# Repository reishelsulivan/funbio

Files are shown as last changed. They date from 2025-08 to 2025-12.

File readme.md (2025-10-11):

# Fundamentos de Biodiseño  
## Grupo 8

<p align="center">
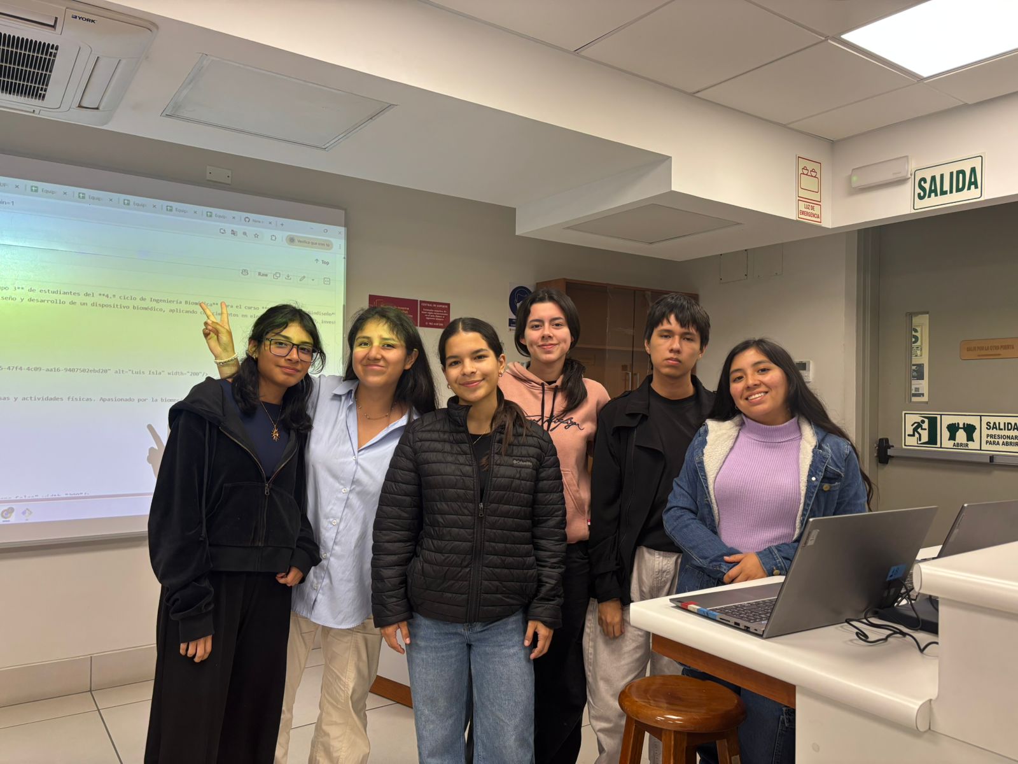
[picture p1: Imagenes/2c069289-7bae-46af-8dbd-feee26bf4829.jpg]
Imagen GRUPAL
  
</p>

*Grupo de estudiantes de Ingeniería Biomédica interesados en el desarrollo de nuevas tecnologías que favorezcan el avance médico.*

---

## 👥 Integrantes

### Reishel Sulivan Lope Paredes  
- **Edad:** 19 años  
<p align="center">
  Imagen REISHEL
</p>

---

### Murga Quispe, Jostin Rájhul  
- **Edad:** 18 años  
<p align="center">
  Imagen JOSTIN
</p>

---

### Daniela Alexandra Ochoa Cieza  
- **Edad:** 19 años  
<p align="center">
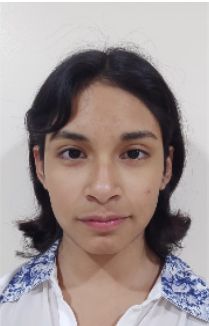
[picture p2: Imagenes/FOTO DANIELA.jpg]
Imagen DANIELA
  
</p>

---

### Sophia Nicole Nieves Maury  
- **Edad:** 21 años
- **Correo:** sophia.nieves@upch.pe 
<p align="center">
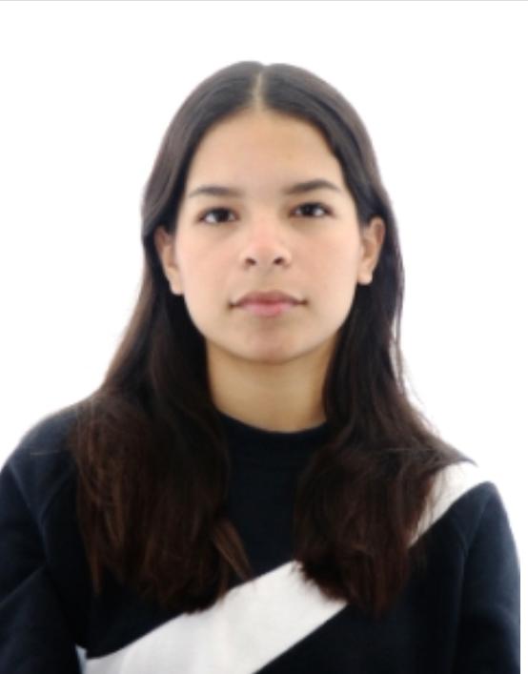
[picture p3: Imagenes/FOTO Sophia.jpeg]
Imagen NICOLE
  
</p>

---

### Sharon Lizeth Oré Arredondo  
- **Edad:** 18 años  
<p align="center">
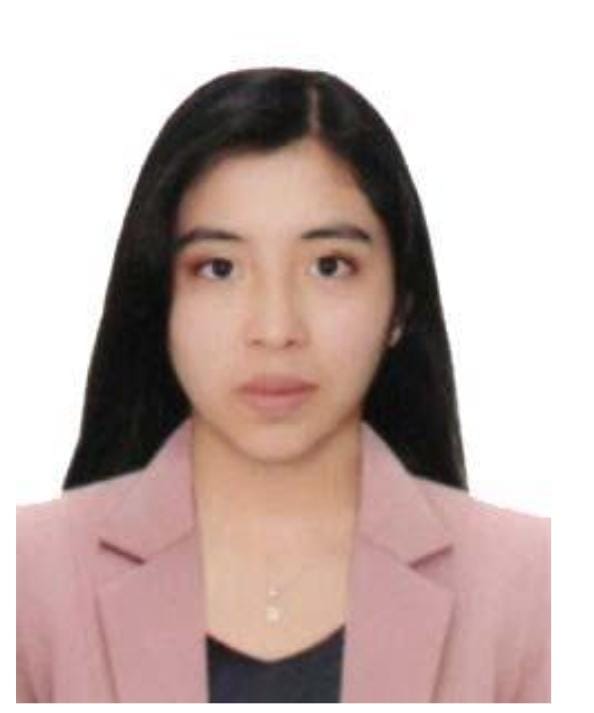
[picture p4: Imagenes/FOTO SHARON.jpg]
Imagen LIZETH
  
</p>

---

### Maria del Carmen Paredes Cavero  
- **Edad:** 20 años  
<p align="center">
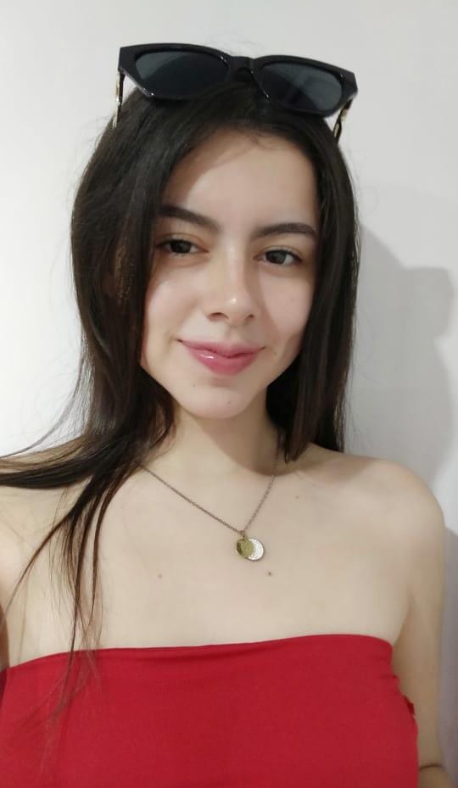
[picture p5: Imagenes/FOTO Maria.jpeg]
Imagen MARIA
  
</p>

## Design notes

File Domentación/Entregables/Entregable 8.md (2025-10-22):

<div align="center">

# Fundamentos de Biodiseño: Entregable Nº 8

</div>
<div align="center">
  
## Sección 2: Modelado 3D
</div>

### Sensor ESP32:
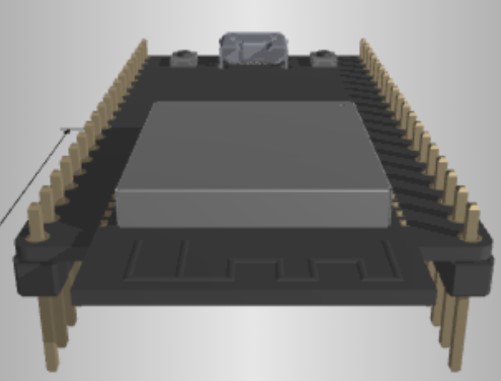
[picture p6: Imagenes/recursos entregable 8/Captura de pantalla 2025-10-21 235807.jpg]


https://cad.onshape.com/documents/9392f3b08a5a12f459dcdf1e/w/5ffc1e2daefd1c3cd6f5d1c5/e/543962da6f37cdc580fbc518?renderMode=0&uiState=68f86065a9befacfd8228599

### Sensor de Temperatura TMP36
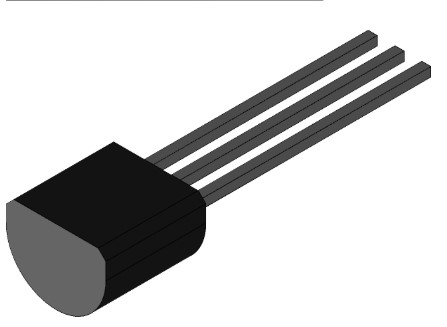
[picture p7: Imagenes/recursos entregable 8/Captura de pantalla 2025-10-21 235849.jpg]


https://cad.onshape.com/documents/74f086d47442c8f6e3b532a9/w/f83696dc04ceff2c60df9320/e/4f5c1f82b5e9618f5d499a5d?renderMode=0&uiState=68f86093083b60e7112f9d35
### FSR 400
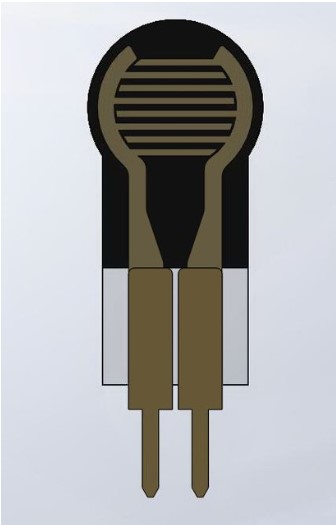
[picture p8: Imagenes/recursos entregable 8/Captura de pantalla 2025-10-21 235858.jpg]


https://cad.onshape.com/documents/1bdf3e697803877b7e2c2b3c/w/df2d8b826d9c72e3113c0d29/e/82d6d8926c4703dbe4e6c42b?renderMode=0&uiState=68f860b1e923a8006b744c4f
### TP4056 module
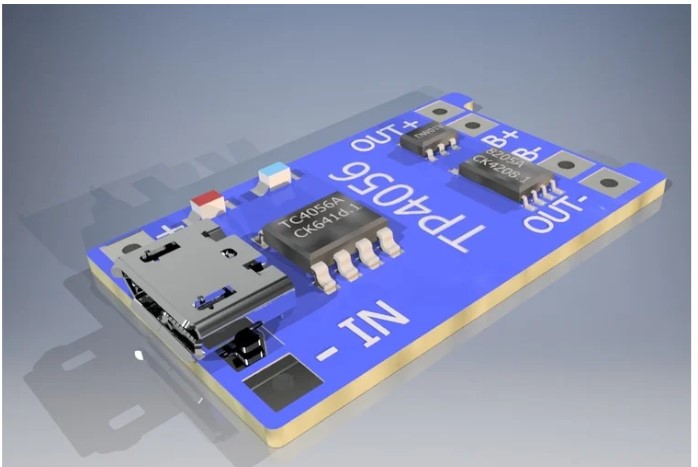
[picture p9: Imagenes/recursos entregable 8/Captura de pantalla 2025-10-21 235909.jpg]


https://cad.onshape.com/documents/18cd05a88509de23cd2a2f93/w/8d196be95ea5bc2b3ad85955/e/2d019528366bb7ebba015902?renderMode=0&uiState=68f863c543911c5820f0d8de
### MT3680 module
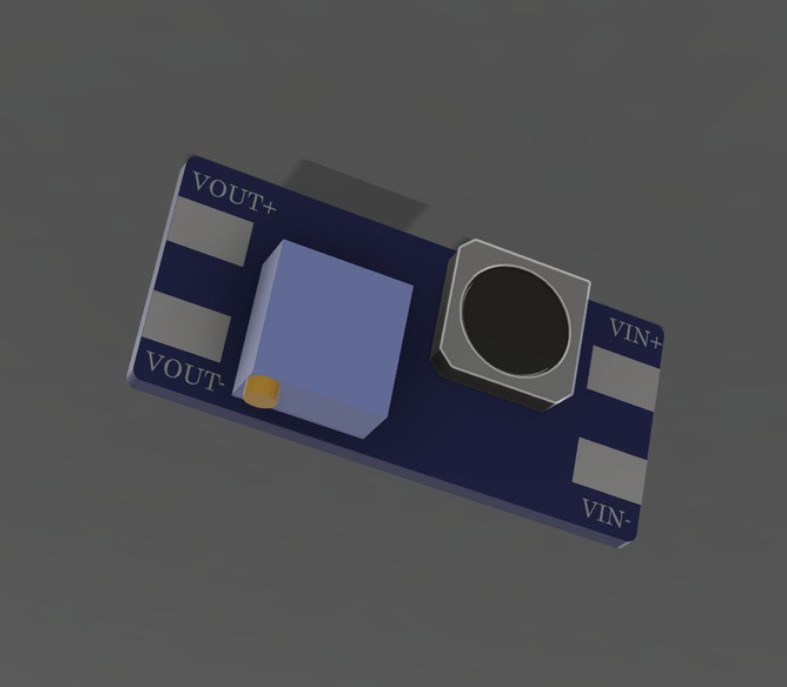
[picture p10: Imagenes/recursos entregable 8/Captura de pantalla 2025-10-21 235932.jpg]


https://cad.onshape.com/documents/760e85918c161715fd75b83e/w/cb98ee53cf6b21a846fe382e/e/080db2f108718dd84d546821?renderMode=0&uiState=68f865730297eada4858e549
### Case Principal
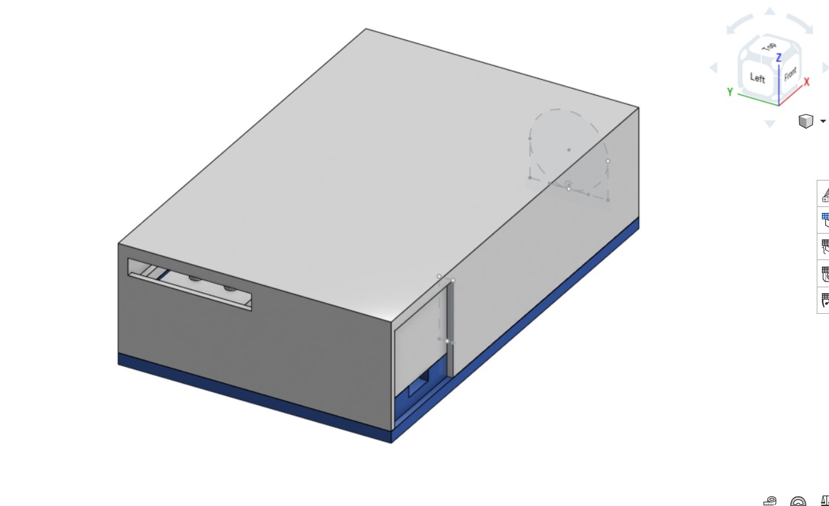
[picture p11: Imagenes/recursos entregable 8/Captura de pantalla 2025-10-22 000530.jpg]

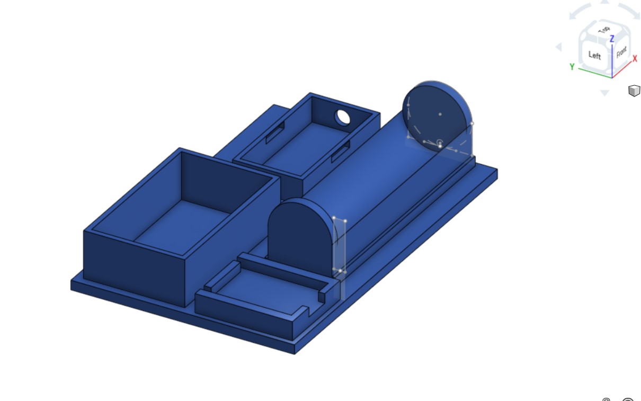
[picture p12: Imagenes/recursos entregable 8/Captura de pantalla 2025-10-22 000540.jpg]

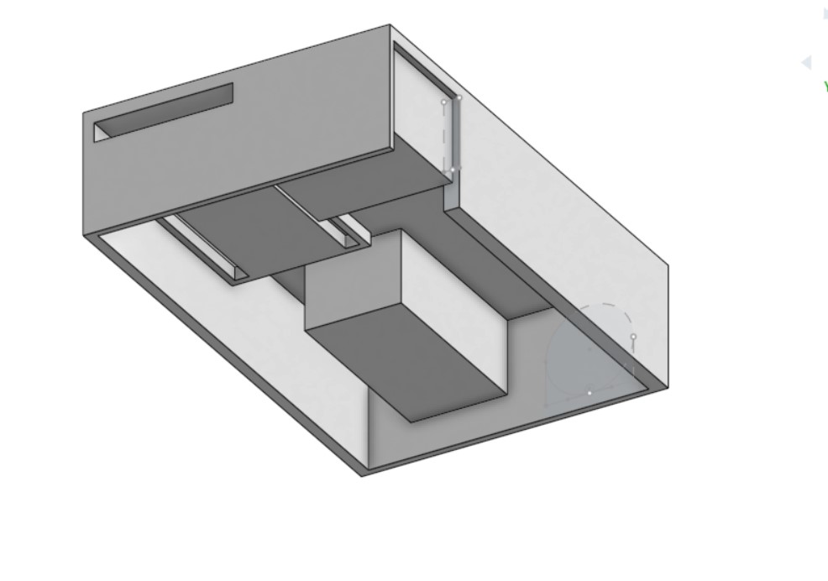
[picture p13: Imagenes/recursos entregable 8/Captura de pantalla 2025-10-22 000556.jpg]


https://cad.onshape.com/documents/a6e36f7cac065b05814f1a20/w/e1e7ecee820c783deadf52ee/e/a61f189e7a23719cba901df4?renderMode=0&uiState=68f8658543911c5820f0db09
### Case FSR
Texto alternativo

### Case Motor de vibracion
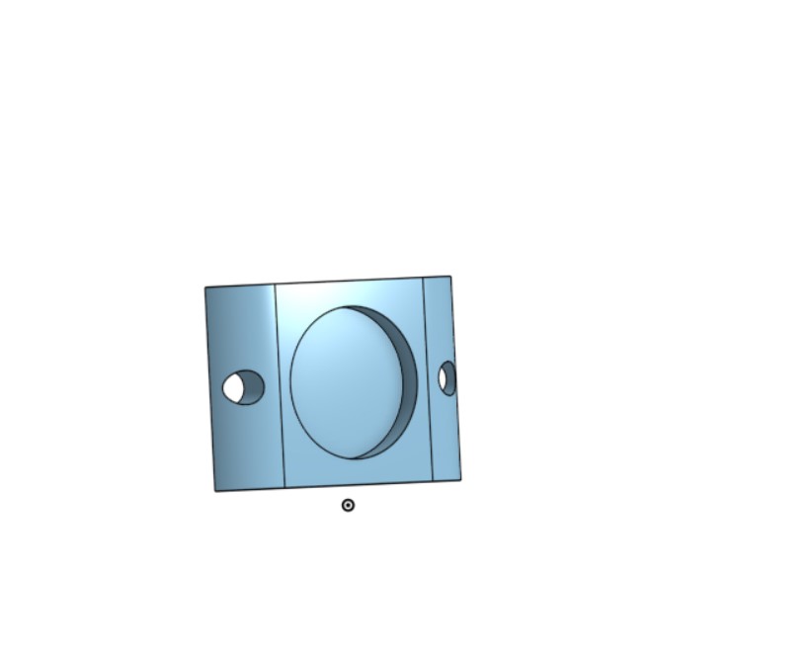
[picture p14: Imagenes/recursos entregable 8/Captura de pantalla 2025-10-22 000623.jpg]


https://cad.onshape.com/documents/7fd997337caf7b52a8c2670a/w/bb5fb6264d26da24b70b61d7/e/f94ade3b7513662598104bfb

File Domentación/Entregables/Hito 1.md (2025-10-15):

<div align="center">

# Fundamentos de Biodiseño: Hito N°1

</div>

<div align="justify">

## 1. Modelos y principios de solución
| **Función**              | **Solución 1**              | **Solución 2**              | **Solución 3**             |
|---------------------------|-----------------------------|-----------------------------|-----------------------------|
| **Distribuir presión**    | Espuma viscoelástica        | Gel de silicona             | Air cushion                 |
| **Reducir fricción**      | Tejido de poliamida         | Tejido de poliéster         | Tejido de algodón           |
| **Absorber sudor**        | Material absorbente         | Canales de ventilación      | Malla 3D transpirable       |
| **Monitorizar presión**   | FSR                         | FlexiForce                  | Sensor capacitivo           |
| **Monitorizar temperatura** | Termistor                 | Sensor infrarrojo           | RTD                         |
| **Fácil poner/quitar**    | Cierre magnético            | Cierre de velcro            | Cremallera                  |
| **Lavable**               | Material impermeable        | Funda desmontable           | Material resistente          |

## 2. Espacio de solución

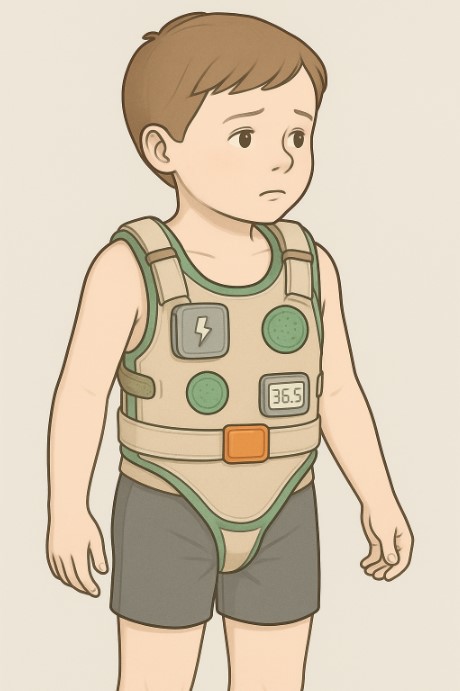
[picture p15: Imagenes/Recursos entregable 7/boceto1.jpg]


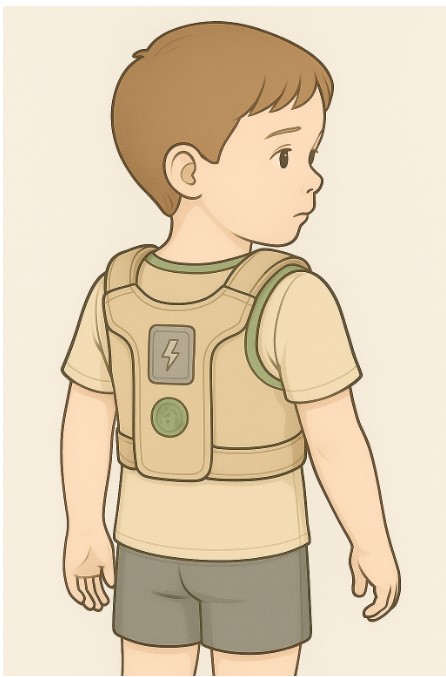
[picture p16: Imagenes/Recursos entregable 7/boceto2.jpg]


## 3. ¿Fabricar o adquirir?:
- Sensor de presión — Adquirir. Se comprará un sensor de presión presente en el mercado, preferiblemente el FSR
- Microcontrolador — Adquirir. Se comprará un microcontrolador ESP32
- Batería - Adquirir
- Carcasa para electrónica - Fabricar. Se fabricará únicamente una carcasa para el microcontrolador y sensores.
- Material para el liner - Adquirir.  Se adquirirá el material del liner.
- Fabricación del liner — Fabricar. Se fabricará el liner con costura.

## 4. Secuencia de procesos:
Describir la rutina clínica de uso del sistema
- Montaje en el paciente
	- El fisioterapeuta prepara la piel del bebé 
	- Se posiciona el liner con sensores dentro del corsé, asegurando que las zonas de presión coincidan con los puntos anatómicos indicados por el médico.
	- Se conecta el módulo electrónico (SPS) a los conectores del liner.
	- Se verifica que todo esté bien colocado y conectado con el recurso de monitoreo
- Calibración
	- Antes de iniciar, se enciende el módulo electrónico y se conecta al recurso de monitoreo.Se realiza una calibración inicial de presión y temperatura, asegurando que las lecturas correspondan al estado de reposo del paciente.
	- Durante esta fase (≈10–15 segundos), el niño permanece quieto para registrar el nivel base de presión y temperatura.
	- A continuación, el fisioterapeuta comprueba la reacción de los sensores ejerciendo suaves presiones manuales en los puntos clave del corsé; el sistema debe mostrar los cambios instantáneamente.
	- Si se detectan lecturas fuera del rango previsto, se ajusta el liner o el corsé hasta alcanzar uniformidad en las áreas sensorizadas.
Se guarda la calibración y se comienza la terapia.
- Sesión de terapia
	- Durante su uso, el sistema mide con el sensor de presión cada 2 segundos y el de temperatura cada 10 segundos, recolectando información suficiente para analizar la distribución de carga y el confort térmico del paciente.
	- Los datos se envían de forma inalámbrica al recurso de monitoreo clínico, donde el fisioterapeuta puede observar las lecturas en tiempo real o analizarlas posteriormente.
	- Si se detecta un aumento de presión o temperatura (por mala colocación o exceso de sudor), el sistema envía una alerta visual en el recurso de monitoreo, indicando la necesidad de reajustar el corsé.
- Desmontaje
	- Se apaga el sistema, se desconecta del liner y se retira cuidadosamente el corsé del bebé.
	- Se retira el liner del corsé si se requiere limpieza o cambio.
- Limpieza:
	- Antes del lavado, se retiran el módulo electrónico (SPS), los sensores removibles, los cuales se limpian por separado con un paño suave humedecido en alcohol isopropílico al 70 % o con toallitas médicas, sin sumergirlos en agua.
	- Una vez limpio y seco, se vuelve a insertar la electrónica en sus respectivos bolsillos sellados y se verifica su funcionamiento mediante el recurso de monitoreo antes del siguiente uso.
**Diagrama de flujo**
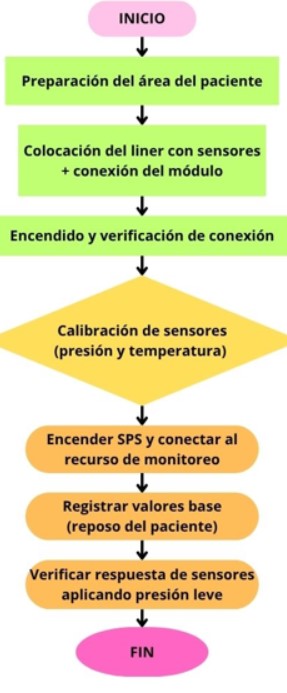
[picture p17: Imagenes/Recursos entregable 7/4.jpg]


## 5. Técnicas de producción

**Electrónica:**
- ESP32.- Se utilizará impresión 3D de polímeros biocompatibles como una carcasa para evitar la incomodidad en el bebé .
  - Costos:  	Debido a que se trabaja con impresión 3D  no requiere de moldes por lo que solo 
		emplea el material necesario sin adicionar costos. Los costos de su producción   
		pueden estimarse entre 2 y 5 dólares por unidad dependiendo del material .
  - Durabilidad: Se optimiza su durabilidad y correcto funcionamiento ya que no se  encuentra expuesto ante caídas o derrame de líquidos .
Facilidad de esterilización: Algunos de los polímeros biocompatibles resisten los procesos de esterilización sin que se dañen o degraden ya que materiales como PETG y PEEK soportan temperaturas de hasta 120 °C. Sumado a esto, se reduce la acumulación de microorganismos debido a su superficie lisa .

## 6. Estaciones de trabajo
Gimnasio  de terapia : Esta estación de trabajo consiste en realizar ejercicios personalizados  de rehabilitación y terapéuticos. Tiene como objetivo recuperar o mejorar la funcionalidad , fuerza o movilidad del paciente .
Es importante que la adquisición del liner vaya acompañada de estas terapias para asegurar una correcta movilidad del paciente de forma cómoda y segura sin riesgo de irritar la piel .
Por otro lado ,para estas sesiones, el especialista debe tener a disposición un dispositivo que le permita monitorear y verificar el correcto funcionamiento del accesorio (ej. bluetooth activado) antes de iniciar con la sesión para evitar incomodidad al momento de realizar los ejercicios. Además , evitar usar en simultáneo equipos de electroterapia o magnetoterapia . 

## 7.Automatización
El sistema cuenta con un nivel medio de automatización, ya que proporciona retroalimentación a través de sensores de temperatura, presión y humedad integrados en el acolchado removible, brindando información útil tanto al grupo médico especializado que supervisa los registros como a los padres o cuidadores, mediante una aplicación comprensible. 
Técnicamente, un nivel medio garantiza que el dispositivo se encargue de interpretar  los datos sensoriales y brinde avisos si se detectan cambios en las condiciones internas (como humedad o temperatura elevada) o presión inadecuada. Esto reduce riesgos y mejora la eficacia del tratamiento, sin reemplazar el criterio profesional. 
Desde el punto de vista clínico, esta elección es adecuada porque el paciente es un niño, y se requiere un equilibrio entre asistencia tecnológica y control humano. El sistema busca facilitar el trabajo terapéutico y permitir al personal especializado evaluar la evolución de la escoliosis congénita del paciente, manteniendo la seguridad y comodidad. Además, la aplicación permite generar reportes diarios, cada tres días o semanales, según lo decida el usuario, facilitando el seguimiento del tratamiento y el monitoreo de la evolución del paciente.
Con respecto a los escenarios de seguridad, en caso de que se detecte una condición anormal —como aumento de temperatura o humedad excesiva— la alerta se enviará automáticamente a través de la aplicación. Esto indica que el sistema está cumpliendo su función de detección. Solo si se presentan falsos positivos, se debe reportar al recurso de monitoreo para que se realice una revisión técnica y se garantice el correcto funcionamiento del dispositivo. Los padres o cuidadores no deben manipular la parte electrónica, ya que requiere conocimientos técnicos.
En caso de falla del sistema, los sensores dejarán de emitir datos y el módulo entrará en “modo inactivo”, evitando lecturas erróneas y posibles confusiones. Por ello, no se requiere un botón de parada de emergencia, debido a que el dispositivo no cuenta con componentes motorizados que representen un riesgo activo. La seguridad se respalda mediante la supervisión del personal especializado y el diseño ergonómico y acolchado del corsé, que evita puntos de presión excesiva y mantiene la comodidad del paciente.

## 8.Interfaces de red global(IoT y telesalud)
### 1.  Sistema y recolección de datos
#### Sensores
i. Sensor de presión (en el punto crítico del corsé): mide la fuerza normal (en Newtons). Su señal analógica entra al convertidor ADC del ESP32 a una tasa típica de 10–50 Hz, lo cual es suficiente para detectar cambios graduales y picos por apriete.
ii. Temperatura del módulo (MCU): un termistor/sensor ubicado cerca de la electrónica/batería para seguridad térmica. Lectura periódica ( cada 1–2 s por ejempl).

#### Microcontrolador ESP32
i. Adquisición: digitaliza presión (ADC) y lee temperaturas (1-Wire/I²C).
ii. Procesamiento: calcula promedios, máximos y banderas (en uso / presión excesiva / temperatura alta).
iii. Reglas con temporización (de esta manera se evitan falsos positivos):
- Uso: presión promedio por encima del umbral de uso durante 2–3 s.
- Presión excesiva: presión por encima del umbral de presión ≥ 3 s.
- Temperatura MCU alta: Tmcu > Tmcu_max ≥ 5 s.
	
iv. Comunicación:
- Bluetooth (activo de manera continua): envía notificaciones inmediatas al celular de los padres. Si el enlace se corta, el ESP32 reintenta y acumula alertas para el siguiente envío.
- Wi-Fi (cuando esté disponible): envía reportes en formato CSV y un resumen de manera diaria a una hora programada o cuando aparece una anomalía.

#### Celular de los padres (Bluetooth)
i. Mantiene una conexión BLE (Bluetooth Low Energy) en segundo plano.
ii. Recibe notificaciones push
- Presión excesiva en el punto
- Temperatura corporal alta
- Módulo caliente, revisar equipo
iii. Muestra el estado (“En uso” / “No en uso”)

#### Servidor/PC del terapeuta (Wi-Fi)
i. Recibe reportes automáticos (diarios o por anomalías) en formato tipo CSV crudo y una hoja de resumen lista para graficar.
ii. Posible inclusión de vistas con curvas de presión/temperaturas y marcadores de eventos.

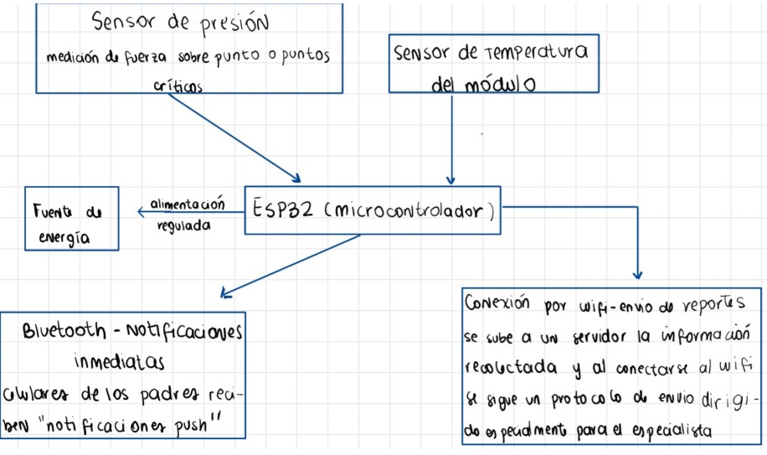
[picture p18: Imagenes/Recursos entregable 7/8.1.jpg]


### 2.  Información recolectada
El sistema registra dos señales y metadatos operativos. En primer lugar, la presión en el punto crítico del corsé (en N), con muestras entre 10 y 50 Hz y suavizada con promedio móvil para atenuar el ruido; a partir de ella se determina el estado de uso cuando el promedio supera un umbral de uso durante algunos segundos, y se detecta presión excesiva cuando la señal permanece por encima del umbral clínico de presión con un tiempo mínimo para evitar falsos positivos. En segundo lugar, la temperatura del módulo electrónico (en °C), medida cerca de la electrónica o la batería a intervalos de 1–2 s, que permite identificar sobrecalentamiento del dispositivo si rebasa el umbral de temperatura por un lapso definido. Además se almacenan metadatos por registro (sello de tiempo, código anónimo del paciente, estado de conectividad Bluetooth/Wi-Fi y eventos como inicio, pausa, fin o alertas) en formato CSV/Excel para análisis y generación de reportes diarios o al detectar anomalías.	

### 3. Reportes para el terapeuta
Esta tabla es el encabezado del reporte que recibirá el especialista. Cada fila resume una lectura con identificadores anónimos y variables clave: Sesión (código de la sesión), Paciente (código anónimo), Fecha en formato ISO (sin ambigüedades horarias), presión_N (fuerza en Newtons sobre el punto monitorizado), temp_modulo_C (temperatura del conjunto electrónico en °C para control térmico), estado_bluetooth y estado_wifi (conectividad al momento de la medición) y en_uso (0/1 según si la presión supera el umbral de uso). Con esta estructura el especialista puede identificar/estudiar rápidamente la adherencia y la comodidad del paciente.



### 4. Medidas de seguridad
Protección de archivos: enviar el CSV/Excel empaquetado en ZIP con contraseña; la contraseña se comparte solo con el terapeuta
Solo recolectar los datos necesarios: solo presión/temperaturas y eventos; nada de datos personales ni ubicación
Registro de fallos: si se detecta sensor desconectado/valores fuera de rango, marcar evento="fallo_sensor" y notificar (de esta manera no arriesgaremos las interpretaciones con lecturas ambiguas)

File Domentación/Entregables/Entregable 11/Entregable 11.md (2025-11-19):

<div align="center">

# Fundamentos de Biodiseño: Entregable Nº 11

</div>

# Introducción
El presente proyecto consiste en el desarrollo de un liner ortésico con sensores destinado a un menor de dos años con escoliosis congénita, con el objetivo de facilitar el monitoreo del crecimiento de la curvatura y la presión ejercida sobre la columna durante el uso del corsé. El sistema integra componentes electrónicos, mecánicos y digitales, combinando sensores de presión (FSR) y temperatura (DS18B20) conectados a un microcontrolador ESP32 para la adquisición y transmisión de datos en tiempo real. 
El liner busca proporcionar información objetiva y continua sobre el comportamiento del cuerpo del paciente en relación a la curvatura. Además, su diseño está orientado a garantizar la comodidad, seguridad y facilidad de uso, tanto para el paciente como para el personal médico.Actualmente, el proyecto se encuentra en la fase de integración y verificación, en la cual se evalúa la compatibilidad entre los subsistemas de hardware, software y manufactura digital, asegurando el cumplimiento de los requerimientos de diseño definidos en etapas previas.

# Objetivos
- Diseñar un corsé inteligente integrado con sensores para monitorear la postura y el crecimiento de la curvatura en la escoliosis congénita en pacientes pediátricos.
- Asegurar un montaje y ajuste rápido del corsé por parte del cuidador para garantizar la comodidad y seguridad.
- Desarrollar una interfaz comprensible para que el cuidador interprete alertas de sobrepresión, batería y fallos del sensor.
- Validar la interacción entre los sensores, el microcontrolador y la interfaz digital con el fin de garantizar una correcta adquisición y transmisión de datos.
- Evaluar el diseño físico y digital del case y las monturas para asegurar la compatibilidad electrónica, comodidad y resistencia del prototipo.
- Verificar el cumplimiento de los requerimientos de diseño y proponer ajustes necesarios antes de la validación final del dispositivo

# Verificación del diseño 
## Hardware (Electrónica) 
### Arquitectura: 
ESP32 DevKit V1 (3.3 V, BLE) + FSR a ADC1 + dos T° (DS18B20 cerca del ESP y TMP36 
alejado) + coin vibrador (PWM) + Li-ion 3.7 V + TP4056 + regulador 3.3 V + switch. 
### Pinout y conexiones: 
Usamos dos sensores de temperatura: DS18B20 cerca del ESP32 para vigilar la T° de la 
placa y TMP36 alejado como referencia ambiental. Con esto detectamos de forma robusta 
posibles sobrecalentamientos del módulo (comparando T_near vs T_amb) y activamos 
protección por firmware. La presión se mide con FSR en ADC1 (GPIO32/33/39) con divisor 
10 k y filtro RC por canal para lecturas estables. El motor de vibración se controla por PWM 
(GPIO18) y se alimenta desde 3.3 V o 5 V mediante MT3608 según requiera el módulo. La 
alimentación sigue: batería → TP4056 → switch → regulador 3.3 V (lógica) y MT3608 5 V 
(motor).  
- Control de temperatura:  
	- DS18B20 (Near-ESP): DQ → GPIO19, 4.7 kΩ pull-up a 3.3 V; VDD 3.3 V; GND 
común. 
	- TMP36 (Ambiental/Far-ESP): Vout → GPIO35 (ADC1_CH7); Vcc 3.3 V; GND.  
- FSR 
	- FSR1 → GPIO32, FSR2 → GPIO33, (FSR3 → GPIO39 si lo usas). 
	- Cada canal: FSR a 3.3 V; nodo → MCU con 1 kΩ serie; 10 kΩ a GND (divisor) + 100 
nF a GND cerca del pin. 
- Vibración 
	- IN → GPIO18 (PWM). Alimentación del módulo a 3.3 V o 5 V con MT3608 (solo 
para el motor). Par +/– trenzado y 100 nF junto al módulo. 
Energía:  
	- Batería 3.7 V → TP4056 → SWITCH → Reg 3.3 V → 3V3 (ESP32, FSR, TMP36, 
DS18B20).

### Lógica térmica (por protección): 
- Disparo si T_near ≥ 50 °C o ΔT = |T_near − T_amb| ≥ 10 °C. 
- Acción: limitar PWM del motor, enviar alerta BLE; registrar evento. 
	
### Verificación:  
- T°: provocar ΔT≥10 °C con aire caliente local al ESP; debe disparar protección.  	
- Autonomía: ≥ 8 h (BLE + logging, sin vibración continua). 	
- Vibración: latencia < 200 ms (GPIO18→corriente).

## Manufactura Digital
 El sistema físico se compone de un case principal impreso en 3D, monturas flexibles para los sensores de presión y soportes internos que integran la electrónica liner.
 Estas piezas han sido diseñadas en Onshape bajo criterios de ergonomía, comodidad de uso y facilidad de integración con los módulos electrónicos (ESP32, sensores FSR, DS18B20, TMP36, TP4056, batería Li-ion y módulo de vibración).
El objetivo del diseño digital es proteger la electrónica, mantener su posición estable sobre el cuerpo, permitir el intercambio o mantenimiento de los componentes.
### Diseño y componentes
#### Case principal:
- Contiene el microcontrolador ESP32 y Expansion Board, el módulo TP4056, MT3608, la batería, el switch y el sensor de temperatura DS18B20.
- Incorpora guías para la fijación de los componentes mediante insertos roscados
- Dispone de ranuras para el acceso a conectores (USB, switch, pines de prueba).
- Protege el conjunto.
- Montura de sensores (FSR):
- Sostiene los FSR en posición estable para estar sujeto en el liner.
- Permiten transmitir la presión del cuerpo sin causar incomodidad ni deformar los sensores.
- 
#### Ensamble general
- Fijar ESP32 y módulos al case mediante insertos roscados
- Conectar batería y guiar los cables
- Insertar el conjunto en el bolsillo o zona designada del liner.
- Conectar las monturas de sensores FSR a los cables del case.

#### Verificación
| **Prueba / Criterio** | **Procedimiento (digital)** | **Resultado esperado** | **Estado** |
|------------------------|-----------------------------|------------------------|-------------|
| **Compatibilidad con electrónica** | Revisión en CAD de los espacios para la PCB, batería y conectores. | Todos los componentes encajan sin interferencias ni solapamientos. |  Verificado digitalmente |
| **Ajuste general del ensamblaje** | Ensamble virtual del case, tapa y monturas en Onshape. | Las piezas se ensamblan correctamente, sin colisiones. |  Verificado digitalmente |
| **Montura de sensores** | Verificación de la ubicación y orientación de los alojamientos para los FSR. | Los sensores quedan bien alineados y en las zonas correctas. |  Verificado digitalmente |
| **Tolerancias de encaje** | Revisión de holguras entre partes (0.2–0.4 mm). | El cierre es firme y permite un ensamblaje suave. |  Verificado digitalmente |
| **Accesibilidad de conectores y botones** | Comprobación visual en el modelo 3D. | Los conectores y botones pueden manipularse fácilmente. |  Verificado digitalmente |
| **Peso y volumen estimado** | Cálculo automático en CAD usando densidad del PLA. | Peso total aproximado ≤ 100 g. |  Por comprobar (físico) |
| **Resistencia y durabilidad** | Análisis preliminar del modelo y espesores. | Estructura sin zonas frágiles; resistencia esperada adecuada. |  Por comprobar (prototipo) |
| **Ajuste en uso prolongado** | Simulación de flexión y contacto con el cuerpo. | No debería causar incomodidad o presión excesiva. |  Por comprobar |
| **Mantenimiento y desmontaje** | Evaluación de apertura y cierre en el modelo. | Se puede abrir sin dañar el encaje ni la tapa. |  Por comprobar |

El diseño digital del case y monturas del liner inteligente ha sido verificado digitalmente y cumple con los requerimientos de diseño, compatibilidad electrónica y ergonomía previstos.
 Se encuentra en fase de validación física tras el envío a impresión 3D.

### Verificación del diseño (Software)
| **N°** | **Funcionalidad** | **Cumplimiento (Sí/No)** |
|:------:|--------------------|:------------------------:|
| 1 | Recepción de datos de temperatura y presión enviados por el microcontrolador ESP32 vía Bluetooth. | Sí |
| 2 | Visualización en pantalla de los valores de temperatura y presión actualizados cada 20–30 minutos. | Sí |
| 3 | Alerta visual cuando los valores de temperatura o presión superan los límites establecidos (por ejemplo, >38 °C o >5 kPa). | Sí |
| 4 | Botón de actualización manual que permite al usuario forzar la lectura de nuevos datos del ESP32. | Sí |
| 5 | Indicador de estado de conexión Bluetooth (conectado / desconectado). | Sí |
| 6 | Registro temporal del historial de las últimas mediciones recibidas. | Parcial |
### Tabla de verificación del prototipo

| **Funcionalidad** | **Cumplimiento** |
|--------------------|------------------|
| Mide las fuerzas aplicadas en tiempo real. |  Sí |
| La interacción de los componentes se acciona mediante los sensores de presión. |  Sí |
| Compara las lecturas de ambos sensores de temperatura para detectar sobrecalentamiento. | Sí |
| Presenta un ahorro de energía para más duración de la batería. |  No |
| Presenta un ajuste de fuerzas automáticas. |  No |
| El dispositivo señala si la temperatura del mismo sobrepasa el rango debido. |  Sí |
| Se ajusta si la presión sensada es menor al rango. |  No |
| Se desajusta si la presión sensada es mayor al rango. |  No |
| El dispositivo emite la información a un sistema de monitoreo. |  Sí |
| La aplicación permite obtener, procesar, transmitir y almacenar datos. |  Sí |

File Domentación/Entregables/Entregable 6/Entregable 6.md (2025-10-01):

<div align="center">

# Fundamentos de Biodiseño: Entregable Nº 6

</div>

<div align="justify">
 
## 1. Situación inicial:	
En la asistencia médica hacia las deformidades de la columna, como la escoliosis, los corsés ortopédicos son una de las intervenciones más indicadas desde una edad temprana. No obstante, en el caso de niños menores de dos años, la adherencia a la terapia presenta desafíos mayores: la piel es más frágil y sensible, el crecimiento del cuerpo es acelerado y el niño no puede comunicar con claridad el dolor o la incomodidad que experimenta. Esto conlleva a que los padres reduzcan el tiempo de uso o quiten el dispositivo con mayor frecuencia, lo que impacta en la efectividad del tratamiento.
La literatura médica indica que una de las causas principales de la baja adherencia al uso de corsés es la incomodidad provocada por puntos de presión excesivos, el calor y la rigidez del material, lo que en etapas tan tempranas se manifiesta en irritaciones en la piel, llanto constante y resistencia al uso prolongado. Asimismo, los diseños comerciales actuales se enfocan en la corrección biomecánica, pero no ofrecen soluciones que combinan confort y un monitoreo objetivo de la presión en áreas críticas.
En este contexto, surge la necesidad de crear un sistema de acolchado interno que, junto con sensores de presión ubicados estratégicamente, facilite la identificación y prevención de la sobrepresión en zonas vulnerables, además de mejorar la comodidad del niño con el dispositivo y, a la vez, registrar el tiempo real de uso y proporcionar retroalimentación. Esta innovación pretende no solo aumentar la adherencia al tratamiento, sino también proporcionar a los profesionales de la salud y a los padres datos información objetiva que les permitan tomar decisiones más seguras en el ajuste y monitoreo del corsé.

## 2. Objetivos estratégicos
### Metas técnicas
Crear un forro acolchado con materiales que sean hipoalergénicos, transpirables y que resulten cómodos para el niño.
Incorporar sensores blandos de presión en las áreas críticas del tronco (pelvis, abdomen y costillas).
Garantizar que el accesorio sea extraíble, lavable y reutilizable sin interferir con la función de corrección del corsé.
Prototipar un sistema elemental de alerta que señale la existencia de presión excesiva.
### Metas económicas
Mantener los costos de producción bajos empleando insumos disponibles en el mercado local (textiles convencionales, espumas para uso médico, sensores piezoresistivos elementales).
Reutilizar los sensores electrónicos para que, al cambiar de corsé o de talla, solo haya que fabricar un nuevo revestimiento acolchado, lo que permite disminuir costos.
Evitar gastos indirectos por dejar el tratamiento, dado que un accesorio más cómodo hace que el niño lo use durante el tiempo correspondiente.
### Metas organizativas
Lograr que el niño se adhiera al tratamiento con mayor facilidad, optimizando su confort y disminuyendo la resistencia a utilizar el corsé.
Integrar la solución en el tratamiento infantil, incorporando el liner como un complemento en su rutina de terapia.
Validar la propuesta en el ámbito académico, mostrando el diseño como opción innovadora y obteniendo comentarios de los alumnos y profesores.
Ofrecer una base para progresos futuros, de forma que el proyecto tenga la capacidad de desarrollarse hacia versiones más sofisticadas con materiales superiores o integración tecnológica.

## 3. Valor añadido 
### Beneficios para el usuario 
- Proporcionar comodidad al momento de usar el corsé baby Boston debido a los  materiales hipoalergénicos y transpirables que son acolchados para reducir la irritación  .Sumado a ello, brinda practicidad al colocar y retirar los sensores al accesorio ya que permite que se pueda lavar sin afectar la funcionalidad de los componentes. 
- Monitorear la adherencia del paciente a través de los sensores que se le colocarán de manera estratégica y permitirán visualizar si la banda es colocada o no.
- Permitir un seguimiento más óptimo en el que se podrán visualizar los datos mediante aplicaciones y comunicación inalámbrica.

### Beneficios para la empresa
- Se reduce el costo de mantenimiento y monitoreo debido a los materiales empleados
- Permite que el dispositivo sea más accesible y brindar a los usuarios un buen  
 producto sin necesidad de intercambiar el corsé que ya se está utilizando .
- Se presenta como un dispositivo innovador en comparación a ortesis tradicionales puesto que prioriza la comodidad de los usuarios sin comprometer la efectividad del tratamiento .

### Beneficios para la sociedad
- Poder hacer uso de cualquier tipo de corsé sin tener que recurrir a ortesis demasiado
costosas.
- Contribuiría a la efectividad del tratamiento , y que además ,al ser utilizado exitosamente, podría evitar futuros procedimiento quirúrgicos en un grado de escoliosis leve .
- Los datos anónimos que se recopilen podrían ayudar a investigaciones sobre la escoliosis y brindar un sistema de retroalimentación mejorado.

## 4. Stakeholders

Son todas las personas o entidades interesadas en el proyecto:

- Usuarios finales (quién usará el sistema).
  - Niños de 1 - 3 años con escoliosis congénita o de inicio temprano, que en principio requieran el uso de corsé como tratamiento conservador.
  - En este caso en particular, niños como Yeferson (1 año y 10 meses) con corsets incómodos, irritables y poco tolerables.
- Clientes (quién lo compra o financia).
  - Hospitales y clínicas (públicas y privadas) que atienden a niños con escoliosis, como el Instituto Nacional de Rehabilitación (INR) en Perú y el Instituto Nacional de Salud del Niño (INSN). 
  - Padres de familia que buscan un tratamiento efectivo y cómodo para sus hijos que tengan problemas de escoliosis con un grado tolerable de curvatura, y tengan la posibilidad de invertir en un accesorio que permita al corsé tener más funciones.
- Partes interesadas clave: médicos, reguladores, fabricantes, aseguradoras, familiares, etc.
  - Médicos: Ortopedistas, fisiatras, neurocirujanos y terapeutas físicos que supervisen el tratamiento. Se necesita su opinión para ver las complicaciones y progresión en los procesos médicos.
  - Fabricantes: Talleres de ortesis que puedan fabricar el corsé. Incorporar la tecnología de sensores y el acolchado para cambiar los procesos tradicionales. Además de ver su experiencia en el modelamiento del cuerpo del niño en esas edades.
  - Familiares: Padres o apoderados que puedan supervisar el uso del corsé y sean capacitados para su uso, además de que pueda financiar el producto para adaptarlo al niño.

- Identificarlos ayuda a entender requisitos y restricciones.
  - Requisitos: Comodidad, efectividad, seguridad, monitoreo de la presión, adaptabilidad al crecimiento, transpirable y bajo costo.

## 5.  Competencias y equipo 
El equipo cuenta con el siguiente conocimiento que adquirió y adquirirá a lo largo del curso:
- Electrónica básica y prototipado con Arduino, lo que permitirá la implementación de sensores biomédicos y circuitos básicos.
- Manejo de sensores, indispensable para el monitoreo de la curva de la columna, además de analizar la comodidad con sensores de temperatura y de humedad.
- Modelado 3D y fabricación digital, facilitará el diseño de carcasas para toda la parte electrónica y previsualizar el resultado final.
- Desarrollo de conectividad básica mediante aplicaciones y comunicación inalámbrica, lo que permite la transmisión y visualización de datos.
- Metodología de diseño (VDI 2221/2206), que estructura el proceso desde la identificación del problema hasta la comunicación de resultados.
Por otra parte, con respecto a los recursos que se cuentan y que es posible la compra de ellos:
- Laboratorios y talleres de electrónica, sensores y fabricación digital (impresión 3D, corte láser).
- Software especializado para diseño esquemático, simulación y modelado 3D.
- Sensores y materiales esenciales previstos para el prototipo:
  - Microcontrolador Arduino
  - Sensores de presión para detectar el ajuste y uso real del corsé.(FSR)
  - Sensor de temperatura para evaluar la comodidad del usuario y confirmar el uso del corsé.
  - Módulo de energía simple (batería recargable o alimentación por USB).
  - Textil compresivo/liner como soporte para integrar los sensores.
  - Carcasa en impresión 3D para proteger la electrónica.
-Asesoría de docentes, que complementan la formación técnica.

## 6. Planificación inicial
### a. Cronograma preliminar
| Fases                     | Descripción                                                                                                                                                                                                 |
|----------------------------|-------------------------------------------------------------------------------------------------------------------------------------------------------------------------------------------------------------|
| Diseño conceptual          | Seleccionar las zonas donde se colocarán los sensores: FSR (costillas, abdomen, crestas ilíacas) y de temperatura. A partir de ello realizar los bocetos del liner teniendo en cuenta la electrónica desmontable. También ver materiales flexibles y lavables para la banda. |
| Adquisición de insumos     | Comprar cada componente y muestras textiles para realizar la banda.                                                                                                                                         |
| Programación básica        | Desarrollar el código para la lectura de FSR y temperatura, aplicar filtros de señal (media móvil) y establecer umbrales simples para definir cuando se está usando o no (conectar con una base de datos que dé la temperatura de la zona) y “presión excesiva”. Probarlo en una superficie controlada para validar funcionamiento básico. |
| Construcción del prototipo | Confeccionar el forro acolchado con bolsillos para ubicar los sensores, integrar los conectores desmontables y preparar una carcasa básica para la parte electrónica.                                         |
| Pruebas técnicas en maqueta | Evaluar el funcionamiento del prototipo colocándolo en un maniquí o superficie controlada. Validar la sensibilidad de los sensores, calibrar los umbrales de presión y humedad y comprobar la estabilidad de las lecturas en condiciones simuladas de uso. |
| Iteración de diseño        | Ajustar la ubicación de los sensores de acuerdo con los resultados iniciales, reforzar costuras del liner, mejorar la estabilidad de las señales y optimizar la disposición de la electrónica desmontable.  |
| Análisis y entrega         | Registrar las gráficas obtenidas (uso horario, presión excesiva, temperatura relativa), documentar el proceso de construcción y presentar el prototipo con las conclusiones y propuestas de mejora.           |

### b. Presupuesto estimado

| Tipo de componente           | Detalle                                                                                                                                             |
|-------------------------------|-----------------------------------------------------------------------------------------------------------------------------------------------------|
| 4–6 sensores FSR              | Los más comunes (FSR 402, Interlink) cuestan entre S/ 45–60 cada uno en distribuidores locales. Si se usan 4 unidades el total quedaría en S/ 180–240. |
| 1 sensor de temperatura       | Digital I2C como MCP9808, TMP117 o LM35 clásico → S/ 25–45.                                                                                         |
| Microcontrolador              | Arduino Nano/Uno ~S/ 95 (precio local). Un ESP32 podría estar entre S/ 110–130.                                                                    |
| Batería + cargador + conectores | Li-Po pequeña 500–1000 mAh + cargador TP4056 → S/ 90–120.                                                                                           |
| Textiles médicos y espumas    | Malla transpirable, espuma médica hipoalergénica → S/ 150.                                                                                          |
| Materiales de prototipado     | Hilo, velcros, bolsillos, impresión 3D básica → S/ 100.                                                                                             |

**Total estimado:** S/ 640–750

### c. Riesgos y mitigación

#### Técnicos
- Lecturas inestables de FSR → mitigación: usar varios sensores y promediar.
- Falsos positivos si el corsé se apoya sobre objetos → mitigación: colocar sensores en zonas clave + combinar con humedad.
- Deriva en humedad en climas extremos → mitigación: usarla solo como criterio adicional, no único.
#### Económicos
- Aumento del costo de textiles médicos → mitigación: prototipar con textiles locales, validar y luego migrar a médicos.
- Daño de sensores en lavado → mitigación: electrónica desmontable (pods).
#### Organizativos
- Poca disponibilidad de voluntarios → empezar con pruebas en maquetas/adultos sanos.
- Tiempo limitado de curso → priorizar MVP: uso/no uso + presión excesiva (lo básico para validación académica).
- 

# Requisitos Funcionales y No Funcionales – Liner

| Categoría principal   | Campo                        | Requisito Funcional y/o No Funcional                                                                                                                                                                                                                                                                                   | Clasificación |
|-----------------------|------------------------------|-------------------------------------------------------------------------------------------------------------------------------------------------------------------------------------------------------------------------------------------------------------------------------------------------------------------------|---------------|
| Función              | Funciones principales y subordinadas | El sistema tiene como función principal monitorear la comodidad del usuario y registrar el tiempo de uso del corsé mediante sensores de presión y temperatura. Cuando se detecten valores dentro de un rango previamente establecido, se confirmará que el corsé se encuentra correctamente colocado. | Must have |
| Función              | Flujos de energía            | El sistema se alimenta a través de conexión directa a USB. De este modo, se asegura autonomía suficiente sin preocuparse por la duración de la batería en etapas tempranas. A futuro se planea integrar una batería recargable de ion/litio.                                                                               | Must have (USB), Should have (batería de ion/litio) |
| Función              | Flujos de material           | El sistema no maneja fluidos ni materiales en gran escala; el principal material es el textil del liner, que debe ser biocompatible, lavable y transpirable para uso prolongado. Las fuerzas transmitidas son las mecánicas entre el cuerpo y el corsé, convertidas en señales eléctricas por los sensores de presión. Además, detectará la temperatura para monitorear el uso. | Must have (liner biocompatible), Must have (detección de presión), Should have (detección de temperatura) |
| Función              | Flujos de información        | El sistema debe adquirir, procesar y transmitir datos de presión y temperatura a un microcontrolador. Los datos se almacenarán temporalmente y podrán visualizarse en una aplicación o mediante indicadores simples (LED o vibración).                                                                                     | Must have |
| Función              | Definición de interfaces     | Los sensores se conectan al microcontrolador a través de cableado básico. Estos miden los parámetros en el liner y transmiten los datos al sistema principal. La comunicación externa se realiza por Bluetooth hacia un dispositivo móvil.                                                                                  | Must have |
| Diseño / Estructura  | Mecánica                     | El liner con sensores debe mantener un espesor máximo de 3 mm para no interferir con el ajuste del corsé Boston.                                                                                                                                                                                                        | Must have |
| Diseño / Estructura  | Eléctrica / Electrónica      | El sistema debe trabajar con un voltaje seguro para contacto humano (3.3–5 V) y contar con protección básica contra cortocircuitos.                                                                                                                                                                                      | Must have |
| Diseño / Estructura  | Ergonomía                    | El liner debe ser transpirable, flexible y lavable para garantizar comodidad al paciente durante un uso prolongado.                                                                                                                                                                                                     | Must have |
| Realización / Producción | Compra                   | El diseño debe tener un costo de fabricación bajo; se deben asegurar los materiales adquiriendo algunos extra como previsión.                                                                                                                                                                                            | Should have |
| Realización / Producción | Fabricación              | El tiempo de creación debe ser proporcional al costo del accesorio, buscando un equilibrio entre ambos.                                                                                                                                                                                                                  | Should have |
| Realización / Producción | Control de calidad       | Debe existir una planeación en software de diseño (ej. Onshape) que asegure precisión en los modelos 3D y facilite un buen ensamblaje de los componentes.                                                                                                                                                                | Should have |
| Realización / Producción | Ensamblaje               | Se debe asegurar la adquisición de piezas en varios puntos de venta, verificando su calidad y réplica exacta para garantizar un ensamblaje correcto.                                                                                                                                                                    | Should have |
| Realización / Producción | Despliegue de software   | Es necesario actualizar el software regularmente para reflejar cambios y mejoras en el sistema.                                                                                                                                                                                                                         | Must have |
| Realización / Producción | Mantenimiento            | Deben existir actualizaciones periódicas para mejorar el prototipo y mantener su funcionamiento en el tiempo.                                                                                                                                                                                                           | Must have |
| Uso                  | Uso                          | El liner debe ser fácil de colocar y retirar de forma segura por los cuidadores, con un sistema simple de ajuste.                                                                                                                                                                                                       | Must have |
| Uso                  | Reciclaje                    | Los sensores deben ser reutilizables para poder integrarse en un nuevo liner cuando el niño crezca.                                                                                                                                                                                                                      | Must have |
| Uso                  | Transporte                   | El liner debe ser liviano y plegable, para que sea fácil y seguro transportarlo junto al corsé.                                                                                                                                                                                                                          | Should have |
| Organización         | Sostenibilidad              | El sistema debe reducir el consumo energético mientras no se utilicen las funciones principales (modo bajo consumo).                                                                                                                                                                                                     | Nice to have |
| Organización         | Mercado                     | El diseño debe mantener costos bajos de producción (menos de S/ 750 por prototipo) para facilitar la escalabilidad.                                                                                                                                                                                                     | Should have |

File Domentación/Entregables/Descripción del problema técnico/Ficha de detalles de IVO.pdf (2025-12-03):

1

Correo: duie.opi@oficinas-upch.pe

## Oficina de Propiedad Intelectual (OPI) Dirección Universitaria de Innovación y Emprendimiento (DUIE)

# Ficha de detalles de la invención

Título de la invención: Integrador de Vigilancia Ortopédica (IVO)

### 1. DESCRIPCIÓN DEL PROBLEMA TÉCNICO

Indique y describa cuál es el problema técnico (o los problemas técnicos) que busca resolver la invención. Se considera problema técnico aquel aspecto técnico (estructura, configuración, entre otros), que antes de la invención no tenía solución o tenía soluciones distintas a la provista por la invención.
En caso de Diseño Industrial, omitir esta parte.

La invención busca resolver un problema técnico relacionado con la verificación, continua y fiable del uso del corsé ortopédico en pacientes con escoliosis, debido a que la efectividad del tratamiento depende del tiempo de uso del dispositivo. En la práctica clínica, esta información suele obtenerse mediante el reporte propio del paciente o de sus cuidadores, métodos que se consideran imprecisos y subjetivos, lo que puede atrasar el tratamiento. Estudios previos han demostrado que la discrepancia entre el uso reportado y el uso real puede ser considerable. Dolan et al. evidenciaron que los pacientes suelen sobreestimar las horas de uso cuando no se emplean dispositivos de registro objetivo, generando una diferencia estadísticamente significativa entre el uso declarado y el registrado electrónicamente [1].

Deficiencias | | técnicas | | en | | soluciones | actuales
Las soluciones existentes para monitoreo de adherencia se basan principalmente en sensores de temperatura alojados dentro del corsé. Sin embargo, investigaciones como las de Rahman et al. señalan que estos dispositivos presentan problemas de exactitud debido a la influencia del clima, la sudoración y la actividad física, factores que generan fluctuaciones térmicas independientes del uso real del dispositivo [2]. Otra deficiencia relevante es la ausencia de monitoreo en tiempo real. Como indica Karol, la falta de sistemas capaces de transmitir información continua limita la capacidad de correlacionar de manera precisa la adherencia con la progresión de la escoliosis, y complica la toma de decisiones clínicas oportunas [3]. Esta carencia resulta especialmente problemática en etapas de crecimiento acelerado, donde el seguimiento constante es crucial. Finalmente, existe una falta de integración entre los datos de los sensores y comunicación con plataformas externas. Aunque se han desarrollado tecnologías aisladas basadas en sensores térmicos o de presión, la literatura coincide en que no se dispone de un sistema portátil totalmente autónomo que combine la detección del uso, el procesamiento inmediato de la información y la transmisión automática hacia cuidadores o especialistas. La ausencia de esta integración obliga a recurrir a dispositivos independientes o revisiones manuales, reduciendo la fiabilidad y utilidad clínica del monitoreo.
Problema | | técnico | que | | aborda | la | invención
El dispositivo propuesto aborda la ausencia de un sistema integral capaz de medir objetivamente el uso de un corsé ortopédico, procesar dicha información en tiempo real y transmitirla de manera continua sin requerir intervención del usuario, lo que resulta fundamental para mejorar la adherencia terapéutica y optimizar los resultados clínicos en pacientes con escoliosis.

REFERENCIAS (IEEE)

[1] L. A. Dolan, S. L. Weinstein, et al., “Brace compliance in patients with adolescent idiopathic scoliosis,”
Spine, | vol. | 29, | no. | 20, | pp. | 2257–2261, | 2004.
[2] T. Rahman et al., “Electronic monitoring of scoliosis brace wear,” J. Pediatr. Orthop., vol. 24, no. 4, pp.
353–357, | | | | | | | 2004.
[3] L. A. Karol, “Effectiveness of bracing in adolescent idiopathic scoliosis and impact of compliance,” J. Pediatr. Orthop., vol. 36, no. 1, pp. 61–66, 2016.

2

### 2. DESCRIPCIÓN DETALLADA DEL INVENTO:

Describa la invención de forma clara enfatizando en qué consiste el concepto inventivo central.
Si la invención es un producto, máquina, equipo y especifique sus partes y cómo se relacionan.
Si la invención es un procedimiento, especifique los pasos, parámetros de operación, insumos, o cualquier otra información relevante para alcanzar el efecto técnico.
La invención puede tener el procedimiento y su producto novedosos por lo que puede detallar los dos. (Mínimo 250 palabras). Incluya figuras, fotografías o diagramas. Adjunte a esta ficha todos las publicaciones u otros documentos asociados que posea al respecto

En caso de Diseño Industrial, adjuntar imágenes o fotos del producto

IVO es un liner instrumentado insertable entre el corsé ortopédico y el torso del paciente que integra sensores de presión y temperatura, procesamiento local, alertas a través de un motor de vibración y comunicación inalámbrica para supervisar y mejorar la adherencia al tratamiento de escoliosis infantil. El dispositivo cuenta con un case para proteger todos los elementos electrónicos y sensores de presión que se adhieren a un revestimiento.

Vista frontal y posterior de IVO | Vista del case de IVO

Fig. 1 Dispositivo IVO en Onshape

Fig. 2. Aplicación Móvil de IVO

3

Liner: soporte textil con cavidades o canales donde se alojan sensores de presión. El liner se fija en el interior del corsé mediante velcro o costuras protegidas.
Sensores de presión (4 unidades): FSR402 colocados horizontalmente a la altura de las costillas (dos a cada lado).
Sensores de temperatura (2 unidades): distribuidos en zonas críticas donde el calor se acumula. Un TMP36 y un DS18B20.
Microcontrolador: módulo ESP32 Recibe continuamente las señales de los cuatro sensores de presión y de los dos sensores de temperatura mediante sus entradas analógicas, las convierte a datos digitales y determina si el corsé está colocado, si la presión aplicada es adecuada y si la temperatura es segura. Una vez procesada la información, el ESP32 activa el motor vibratorio cuando se supera un umbral de presión o temperatura. Además, gracias a su conectividad WI-FI, transmite en tiempo real los datos de uso hacia la aplicación móvil, donde los cuidadores pueden visualizar los datos de los sensores. Esto permite supervisión continua sin intervención del usuario y sin necesidad de módulos adicionales.
Actuador háptico: motor de vibración montado fuera del case; se activa en dos eventos: sobrepresión y sobretemperatura.
Fuente de energía y gestión: batería LiPo recargable, TP4056 y MT3068.
Case y encapsulado: caja compacta con aislamiento térmico y mecánico, fijada al liner en zona lateral para evitar molestias. Conectores o trazas flexibles (flex PCB) unen sensores al case.
Software / App: Aplicación móvil (BLE): muestra si es dispositivo se está utilizando y los datos de los sensores
Case Principal: El case principal es una carcasa compacta que aloja la electrónica del sistema, incluyendo el ESP32, los módulos de alimentación y las conexiones de los sensores. Su función es proteger los componentes frente a golpes, polvo y manipulación externa, además de organizar el cableado y permitir una salida limpia hacia los sensores. El diseño considera espacio para ventilación básica, montaje seguro y acceso a los puertos necesarios. Fue impreso en 3d con el material PLA.

Fig 3. Case junto a la electrónica ensamblada

4

### 3. DESCRIPCIÓN DE LOS ANTECEDENTES

Liste y describa los productos, procedimientos más parecidos a su proyecto y los principales antecedentes técnicos o bibliográficos que haya consultado. Explique cuáles fueron los principios técnicos en los que se inspiró para obtener la invención; o que usó y estudió durante el proceso de investigación que dio como origen al proyecto. Pueden ser papers, tesis, vídeos, documentos, libros, etc.

Patentes relevantes
Las innovaciones recientes en ortesis inteligentes buscan mejorar la medición del uso real del corsé y optimizar su ajuste mediante sensores y conectividad. Una de las referencias más relevantes es la patente US20240139017A1, que describe un corsé para escoliosis equipado con vejigas inflables, sensores de presión, una unidad de procesamiento y conectividad inalámbrica, permitiendo registrar la presión ejercida y
analizar | la | adherencia | mediante | plataformas | externas | [1].
Otra contribución importante es la patente US20220226140A1, la cual integra sensores de presión dentro del corsé y un módulo de control que procesa la información, se comunica con un dispositivo externo y ofrece retroalimentación inmediata para mejorar el ajuste y fomentar el cumplimiento terapéutico. Incluye además
elementos | de | gamificación | para | aumentar | la | motivación | del | paciente | pediátrico | [2].
Asimismo, la patente WO2023126559A1 propone un dispositivo ortésico dinámico basado en bandas elásticas correctivas y sensores conectados por Bluetooth, orientado a mejorar la comodidad y registrar en tiempo real la presión aplicada a lo largo del tratamiento [3].
Productos comerciales
En el mercado existen soluciones que implementan monitoreo objetivo del uso del corsé. ThermoBrace (ISICO) es un sistema de monitoreo por temperatura ampliamente referenciado en la práctica clínica que registra las horas reales de uso del corsé para evaluar adherencia y ajustar el tratamiento; su empleo ha sido documentado en estudios clínicos y revisiones sobre cumplimiento de bracing [4], [6]. Boston Sensor es un dispositivo comercial que se aloja en el corsé (modelo Boston) y registra la temperatura interna para estimar los patrones de uso; su fabricante lo promociona como herramienta de mejora de la adherencia integrada al brace Boston [5]. Recientemente se han presentado nuevos desarrollos comercial-clínicos como Cor-Esc (Cor-Esc-25), un módulo diseñado para instalarse en distintos corsés que combina sensores de temperatura y presión con conectividad Bluetooth para ofrecer datos objetivos sobre el uso y ajuste del brace [7]. Otro producto con enfoque en telemetría clínica es ScolioSense, un sistema certificable que integra sensores en el brace y una plataforma móvil/web para monitorizar en tiempo real la colocación, el ajuste y la adherencia del paciente [8].
Soluciones open-hardware y plataformas modulares
El desarrollo de sistemas open-hardware ha permitido explorar alternativas más accesibles para el monitoreo del corsé. Se han implementado módulos basados en sensores FSR, IMU y sensores piezoeléctricos conectados a microcontroladores como ESP32 o Arduino, capaces de registrar presión, postura y movimiento. Estas soluciones han sido usadas en investigaciones debido a su bajo costo, facilidad de integración en corsés comerciales y capacidad de transmitir datos mediante Bluetooth Low Energy hacia aplicaciones móviles. Aunque estas plataformas aportan flexibilidad y adaptabilidad, aún carecen de estandarización clínica y suelen presentar variabilidad en la precisión de los sensores.
Referencias
[1] U.S. Patent US20240139017A1, “Corset for scoliosis with inflatable pressure bladders,” D. B. McCoy, 2024.
[2] U.S. Patent US20220226140A1, “Back brace and system for treatment management,” C. Geremtzes et
al., | | | | | | | | | | 2022.
[3] WO Patent WO2023126559A1, “Dynamic compression orthotic device with sensors,” C. Gutiérrez San
Román | | | et | | | al., | | | | 2023.
[4] S. Donzelli et al., “Adolescents with idiopathic scoliosis and their parents have differing attitudes toward the brace: compliance monitoring and clinical impact,” Scoliosis and Spinal Disorders, 2017. Available: https://scoliosisjournal.biomedcentral.com/articles/10.1186/s13013-017-0119-x.
[5] Boston O&P, “Boston Sensor — Improve Scoliosis Brace Compliance,” product page. Available: https://www.bostonoandp.com/products/scoliosis-and-spine/boston-sensor/.
[6] ISICO, “ThermoBrace / use of temperature sensors to monitor brace wear,” ISICO resources. Available: https://en.isico.it/isico/ricerca/pdf/ID00680.pdf and https://en.isico.it/2019/01/01/scoliosis-a-sensor-for-better-bracing-treatment/. (https://en.isico.it/2019/01/01/scoliosis-a-sensor-for-better-bracing-treatment/)

5

[7] “Cor-Esc-25: dispositivo para monitorización del corsé,” Farmacosalud / ConSalud / La Razón (informes de prensa sobre Cor-Esc-25), 2025. Examples: https://farmacosalud.com/creado-un-dispositivo-que-mejora-el-tratamiento-de-la-escoliosis-idiopatica-en-el-adolescente/ (https://farmacosalud.com/creado-un-dispositivo-que-mejora-el-tratamiento-de-la-escoliosis-idiopatica-en-el-adolescente/) and https://www.consalud.es/saluddigital/innovacion-tecnologica/nuevo-dispositivo-permite-mejorar-el-tratamiento-de-la-escoliosis-idiopatica-del-adolescente.html.
[8] Aidplex Scoliosis, “ScolioSense — smart wearable device for real-time monitoring of scoliosis braces,” product and documentation pages. Available: https://scoliosense.com/ (https://scoliosense.com/?utm_source=chatgpt.com) and https://apps.apple.com/gr/app/scoliosense/id1534689026.

6

3.1.¿Conoce algún trabajo o invento que se parece más a su invento? Si la respuesta es afirmativa, enumerar, indicando el nombre de la publicación, la fuente y fecha de publicación y adjuntar un breve resumen de dicho antecedente.

3.2 Si Ud. ha identificado la existencia de un antecedente más cercano en el punto 3.1, señale cuáles son las características técnicas novedosas de su Invento en relación con dicho(s) antecedente(s). De preferencia limite este comparativo solo a los tres antecedentes que considere más cercanos en el aspecto técnico y científico a su invención (el estado de la técnica).

No, al contrario. Durante la investigación, se encontraron diversas patentes que ya evidenciaban un amplio desarrollo en corsé ortopédicos. En consecuencia, optamos por desarrollar un liner ya que se podría adaptar a cualquier corsé y mejora la experiencia del usuario.

7

### 4. VENTAJAS DE LA INVENCIÓN

Detalle las ventajas que tiene la invención respecto a los antecedentes. Las ventajas podrían ser: mayor sensibilidad, especificidad, no presenta efectos secundarios, menor tiempo de diagnóstico, etc.

1. Monitoreo objetivo y cuantificable del uso del corsé

IVO proporciona mediciones directas (presión y temperatura), sustituyendo el autoreporte. Esto permite conocer la calidad del ajuste, reduciendo la incertidumbre clínica y mejorando la toma de decisiones terapéuticas.

2. Detección en tiempo real de colocación/retirada y desajustes

El procesamiento local por el ESP32 permite identificar inmediatamente si el liner ha sido retirado o si la presión aplicada está fuera de los rangos establecidos. Esta detección temprana posibilita intervenciones oportunas (alertas al cuidador o ajustes inmediatos), disminuyendo periodos sin tratamiento efectivo.

3. Retroalimentación háptica inmediata para el paciente

El motor de vibración activa señales locales cuando se detectan sobrepresión o sobretemperatura, ofreciendo una corrección inmediata sin necesidad de supervisión externa. Para niños reacios o con baja tolerancia, la vibración puede reducir la necesidad de intervención directa y promover autocorrecciones o recordatorios discretos.

4. Supervisión remota mediante aplicación móvil

La transmisión WIFI hacia una app permite que cuidadores visualicen datos en tiempo real. Esto facilita el seguimiento entre citas clínicas, mejora la comunicación cuidador-clínico y posibilita intervenciones a distancia.

5. Mejora de la seguridad del paciente

El monitoreo de temperatura del módulo y alertas por sobrecalentamiento previenen riesgos de irritación o lesión cutánea.

6. Diseño modular y potencial de compatibilidad con múltiples corsés

Al diseñarse como un complemento que puede integrarse dentro del corsé, IVO favorece la reutilización entre modelos y reduce la necesidad de rediseñar el corsé completo. Esto facilita su adopción en distintos centros y pacientes.

7. Confort y aceptabilidad mejorados

Sensores delgados y un case compacto reducen la intrusividad del sistema. Menor volumen y posibilidad de miniaturización aumentan la tolerancia en niños, disminuyendo rechazo y mejorando la adherencia por confort físico.

9. Configurabilidad clínica y personalización del tratamiento

Umbrales de presión y temperatura configurables adapte los parámetros al caso particular del paciente.

10. Facilita mantenimiento y escalabilidad

Arquitectura modular (sensores reemplazables, case con acceso) simplifica reparaciones y actualizaciones. Esto reduce costos de mantenimiento y permite escalar la solución a programas clínicos más amplios.

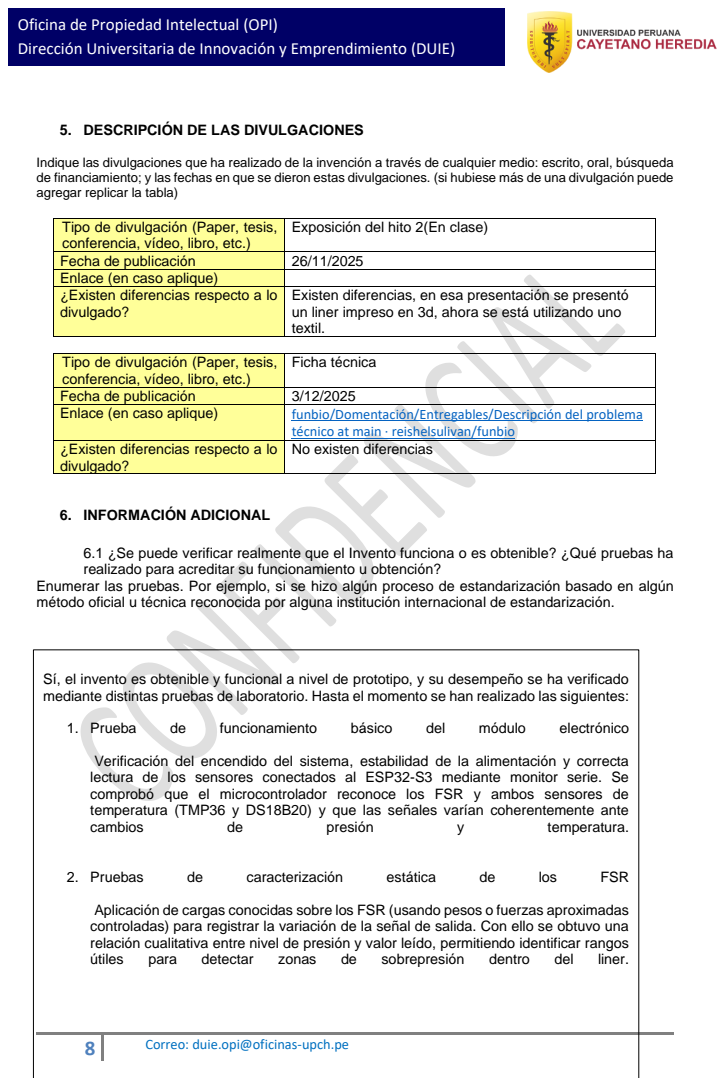
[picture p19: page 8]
6. INFORMACIÓN ADICIONAL; 1. Prueba; funcionamiento; básico; del; módulo; electrónico; cambios; presión; temperatura.; 2. Pruebas; caracterización; estática; los; FSR; útiles; para; detectar; zonas; sobrepresión; dentro; liner.

5. DESCRIPCIÓN DE LAS DIVULGACIONES

Indique las divulgaciones que ha realizado de la invención a través de cualquier medio: escrito, oral, búsqueda
de financiamiento; y las fechas en que se dieron estas divulgaciones. (si hubiese más de una divulgación puede
agregar replicar la tabla)

Tipo de divulgación (Paper, tesis, conferencia, vídeo, libro, etc.) | Exposición del hito 2(En clase)

Fecha de publicación | 26/11/2025
Enlace (en caso aplique)
¿Existen diferencias respecto a lo divulgado? | Existen diferencias, en esa presentación se presentó un liner impreso en 3d, ahora se está utilizando uno textil.

Tipo de divulgación (Paper, tesis, conferencia, vídeo, libro, etc.) | Ficha técnica

Fecha de publicación | 3/12/2025
Enlace (en caso aplique) | funbio/Domentación/Entregables/Descripción del problema técnico at main · reishelsulivan/funbio (https://github.com/reishelsulivan/funbio/tree/main/Domentaci%C3%B3n/Entregables/Descripci%C3%B3n%20del%20problema%20t%C3%A9cnico)

¿Existen diferencias respecto a lo divulgado? | No existen diferencias

6.1 ¿Se puede verificar realmente que el Invento funciona o es obtenible? ¿Qué pruebas ha
realizado para acreditar su funcionamiento u obtención?

Enumerar las pruebas. Por ejemplo, si se hizo algún proceso de estandarización basado en algún
método oficial u técnica reconocida por alguna institución internacional de estandarización.

Sí, el invento es obtenible y funcional a nivel de prototipo, y su desempeño se ha verificado
mediante distintas pruebas de laboratorio. Hasta el momento se han realizado las siguientes:

Verificación del encendido del sistema, estabilidad de la alimentación y correcta
lectura de los sensores conectados al ESP32-S3 mediante monitor serie. Se
comprobó que el microcontrolador reconoce los FSR y ambos sensores de
temperatura (TMP36 y DS18B20) y que las señales varían coherentemente ante

Aplicación de cargas conocidas sobre los FSR (usando pesos o fuerzas aproximadas
controladas) para registrar la variación de la señal de salida. Con ello se obtuvo una
relación cualitativa entre nivel de presión y valor leído, permitiendo identificar rangos

9

3. Pruebas | de | respuesta | térmica | y | monitoreo | de | sobrecalentamiento

Comparación de las lecturas del TMP36 y del DS18B20 frente a una referencia (termómetro comercial) en distintas condiciones de ambiente y contacto. Además, se hizo funcionar el ESP32-S3 por periodos prolongados para observar el aumento de temperatura y validar que el sistema es capaz de detectar posibles
sobrecalentamientos | del | módulo.
4. Pruebas | de | integración | en | el | liner

Montaje del sistema sensorial y el módulo electrónico sobre la estructura textil del liner y pruebas sobre un soporte físico que simula el torso. Se verificó la continuidad de las lecturas en diferentes posturas y ajustes, así como la estabilidad mecánica de las conexiones.

5. Pruebas | de | adquisición | y | registro | de | datos

Ensayos de adquisición continua durante un intervalo de tiempo usando la aplicación, revisando que no haya pérdidas de señal y que los datos puedan exportarse o
visualizarse | | correctamente | para | futuros | | análisis.

Si bien aún no se ha realizado un proceso de estandarización formal bajo una norma internacional específica, las pruebas se han basado en procedimientos de calibración y verificación descritos en literatura técnica y en las hojas de datos de los fabricantes de los sensores.

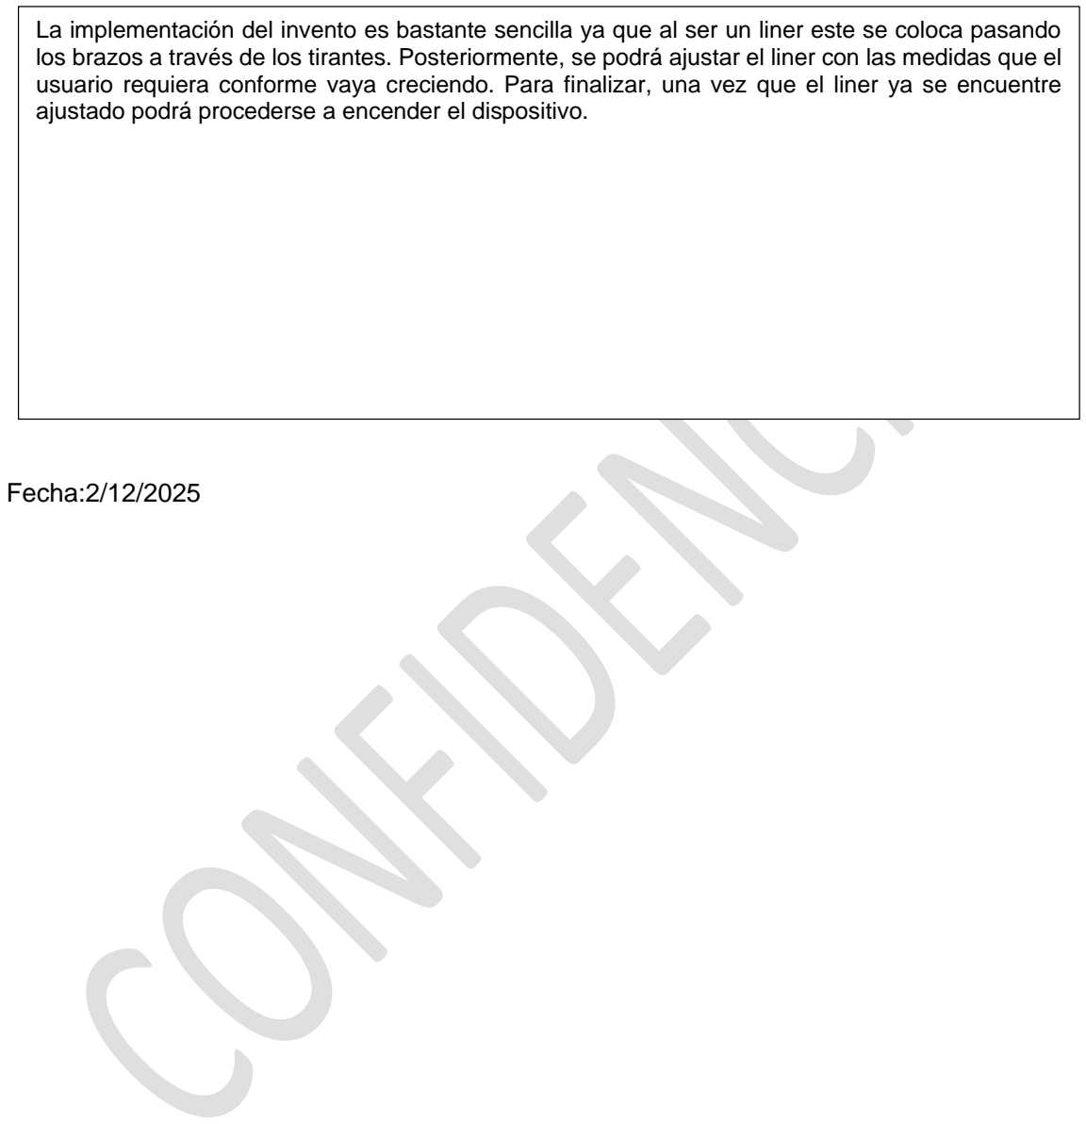
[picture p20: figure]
Fecha:2/12/2025

### 10 Correo: duie.opi@oficinas-upch.pe

6.2 Explique en un (1) párrafo como máximo. Cómo se llevaría a cabo la implementación del invento (Resultaría fácil poder implementar al momento de usarlo, explique porqué).

La implementación del invento es bastante sencilla ya que al ser un liner este se coloca pasando
los brazos a través de los tirantes. Posteriormente, se podrá ajustar el liner con las medidas que el usuario requiera conforme vaya creciendo. Para finalizar, una vez que el liner ya se encuentre ajustado podrá procederse a encender el dispositivo.

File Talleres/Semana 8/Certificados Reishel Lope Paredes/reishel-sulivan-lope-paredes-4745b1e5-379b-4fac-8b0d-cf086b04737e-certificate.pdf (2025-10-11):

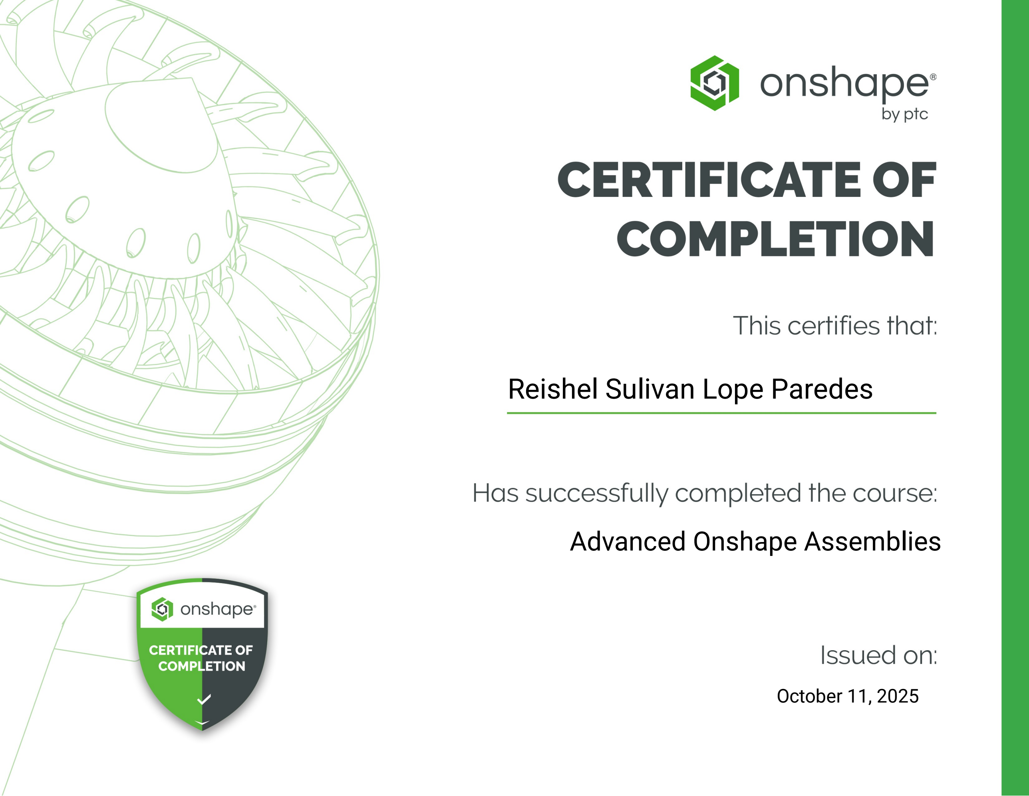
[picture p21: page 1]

Reishel Sulivan Lope Paredes

Advanced Onshape Assemblies

October 11, 2025

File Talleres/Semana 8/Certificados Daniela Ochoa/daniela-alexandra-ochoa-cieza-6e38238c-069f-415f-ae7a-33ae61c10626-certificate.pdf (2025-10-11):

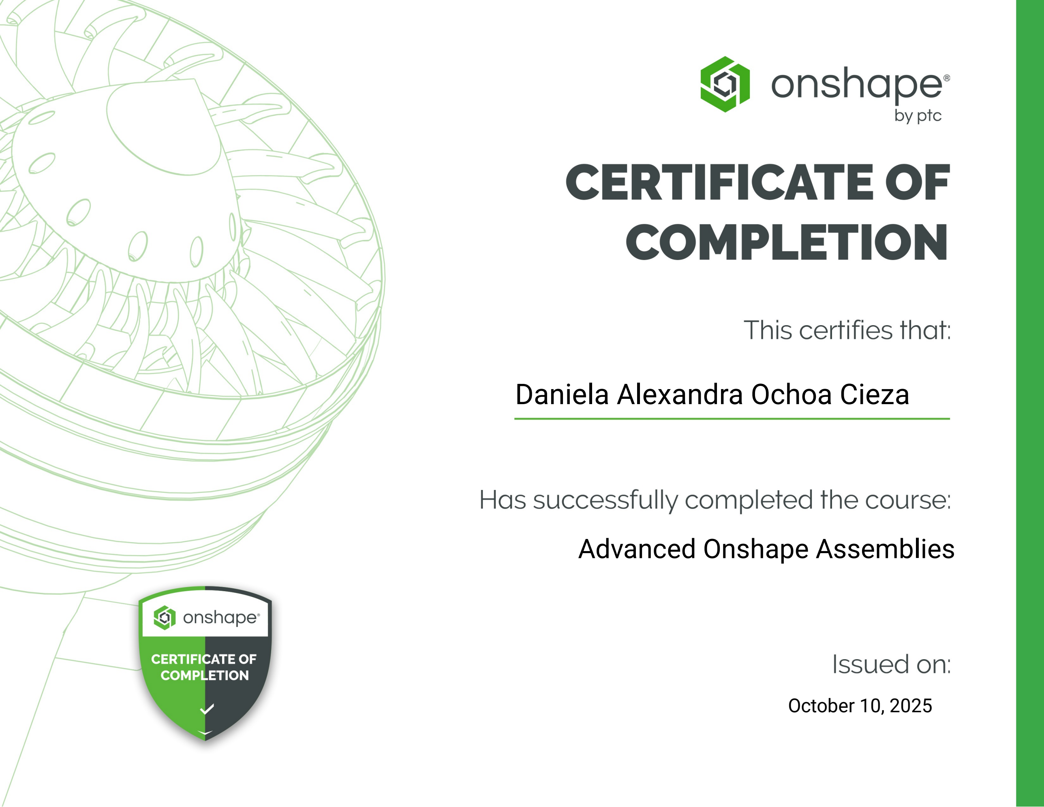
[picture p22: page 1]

Daniela Alexandra Ochoa Cieza

Advanced Onshape Assemblies

October 10, 2025

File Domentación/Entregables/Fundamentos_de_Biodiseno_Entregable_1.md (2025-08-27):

<div align="center">

# Fundamentos de Biodiseño: Entregable Nº 1  

</div>
<div align="center">
  
## Grupo 8

</div>

### Integrantes:
- Sophia Nicole Nieves Maury
- Daniela Alexandra Ochoa Cieza
- Reishel Sulivan Lope Paredes
- Maria del Carmen Paredes Cavero
- Murga Quispe Jostin Rájhul
- Sharon Lizeth Oré Arredondo

## Enfermedades:

## Lesión medular

### Ficha de la enfermedad
La lesión medular es una condición neurológica dada por una patología o evento que discapacita el sistema nervioso central. Se divide en dos categorías: traumáticas y no traumáticas. Con respecto a la primera, estas se dan por eventos traumáticos y específicos, tales como accidentes de tráfico, caídas o acontecimientos de carácter agresivo. Por otro lado, respecto a la del segundo tipo, puede darse por una causa patológica específica que afecte la médula espinal. Si bien es menos frecuente, existen casos en los que ha ocurrido, ya sea por tumores, enfermedades vasculares, infecciones graves, enfermedades degenerativas o autoinmunes. En ese sentido, el mayor padecimiento ocurre en el sistema nervioso central (SNC), lo cual conlleva a que el sistema motor y sensitivo también se vean afectados, ya que en la mayoría de los casos se pierde cierto grado de sensibilidad ante estímulos externos y capacidades motoras en determinadas zonas del cuerpo. A nivel anatómico, las lesiones medulares que se dan por eventos abruptos, interrumpen la continuidad de la médula espinal (la cual trasciende desde el bulbo raquídeo hasta la costilla L1-L2 en adultos) debido a la energía del trauma, lo que, en primera instancia, puede llevar a necrosis o hemorragias internas. Posteriormente, las neuronas suelen sobreexcitarse, lo que conduce a la muerte neuronal programada de estas y a la generación de radicales libres, afectando aún más a las células neuronales. A nivel fisiológico, se bloquea la conducción nerviosa por debajo de la zona afectada, se alteran reflejos y se comprometen funciones autónomas del cuerpo, desde motricidad hasta funcionamientos cardiovasculares, por ejemplo.

### Factores y análisis de la enfermedad
Entre los principales factores de riesgo de las lesiones medulares se encuentran los accidentes automovilísticos, las caídas, intentos fallidos de suicidio, la práctica de deporte de alto impacto, carga de objetos pesados, entre otros. De esta manera, estos eventos suelen afectar la capacidad sensitiva, motora, y autonómicas de aquel que la padece, donde se comprometen los brazos, el tronco, las piernas, la coordinación motora, ocurren diferentes disfunciones como la sexual, vesical o intestinal e inestabilidades cardiovasculares o respiratorias. Sobre esa base es que la calidad de vida de las personas con lesiones medulares se encuentra profundamente expuesta, ya que el manejo de la vida de estos individuos cambia radicalmente. Las mayores dificultades radican en la pérdida de autonomía y de sensibilidad,donde eventos como sentir calor, frío o el tacto de un familiar, la consciencia sobre la propiocepción, hacer necesidades por uno mismo o incluso acomodarse la almohada para mayor comodidad se convierten en acontecimientos irrepetibles para el individuo en cuestión. Sin dudas, es una condición traumática no solo para el cuerpo, sino también para la mente.

### Prevención, diagnóstico, tratamiento y monitoreo
A pesar de que existan acontecimientos que no se pueden prever del todo, sí es posible realizar cambios que influyen en la cotidianeidad de la gente, como una buena educación vial, prevenciones de caídas en adultos mayores y protocolos de riesgo y cuidado para trabajos o deportes extremos. Estas prácticas pueden marcar una diferencia en la vida de muchas personas, así como chequeos frecuentes y avances en la medicina ante tumores espinales y enfermedades autoinmunes.  

Por otro lado, una vez dado el evento, se realizan distintas evaluaciones neurológicas para conocer el nivel de funcionamiento motor y sensitivo para poder determinar la gravedad de la lesión, como la prueba **ASIA (American Spinal Injury Association)**, o exámenes de señales médicos, como resonancia magnética, TAC e imagenología.  

Posterior a esta etapa, se busca inmovilizar el cuerpo hasta saber exactamente la gravedad, ya que mínimos movimientos podrían comprometer otras partes de la médula espinal. Una vez haya pasado esta fase, las terapias de rehabilitación física suelen ser una muy buena opción para muchas personas, pero existen casos en donde, a pesar de que se sabe que no habrá mejoría, esta debe hacerse igual ya que no se puede dejar a las extremidades sin movimiento alguno.  

Además, se han desarrollado bastantes métodos de tratamiento, como **estimulaciones neuronales, terapia con células madre o biomateriales y exoesqueletos robóticos**. Todo ello debe ir acompañado de un proceso psicológico y apoyo de personas cercanas ya que, como se ha mencionado anteriormente, es un evento sumamente traumático para el paciente a nivel mental.  

De esta forma se logra **monitorear el avance del paciente**, a través de un acompañamiento integral, exámenes complementarios de imagenología y terapia física.

### Reflexión ingenieril
Finalmente, las lesiones medulares representan un reto médico, clínico y, sobre todo, personal para el paciente. Pero también puede llegar a ser una oportunidad, un nicho de investigación en donde los ingenieros pueden replantearse el papel de la tecnología en afecciones comúnmente manejadas por la medicina tradicional.  

Desde la perspectiva de la **ingeniería biomédica** es necesario saber que nuestro papel va mucho más allá de la creación de dispositivos, la carrera es humanizadora y las lesiones medulares nos permiten centrarnos en la anatomía, fisiología, y la calidad de vida de las personas que la padecen.  

Desde la recuperación de la movilidad y de la autonomía hasta la prevención de complicaciones secundarias, como úlceras, espasmos o dolor neuropático.
## Lesión medular

### Referencias:
1. J. F. Cañar-Camacho, A. A. Ramírez-Coronel, L. A. Romero Sacoto, M. Á. Estrella González, y É. A. Maxi Maxi, “Factores de riesgo y prevalencia de la lesión medular en adultos: una revisión sistemática,” *Rev. Multidiscip. Investig. Contemp.*, vol. 1, no. 2, pp. 76–97, 2023, doi: [10.58995/redlic.v1i2.n30](https://doi.org/10.58995/redlic.v1i2.n30).  

2. M. J. Arroyo Espinal, *Calidad de vida en personas con lesión medular*, Tesis Doctoral, Univ. Complutense de Madrid, Facultad de Psicología, Madrid, España, 2015. [En línea]. Disponible en: [https://docta.ucm.es/rest/api/core/bitstreams/896ebcb1-d30d-43ae-9814-cc29b2ac9380/content](https://docta.ucm.es/rest/api/core/bitstreams/896ebcb1-d30d-43ae-9814-cc29b2ac9380/content).  

3. J. C. Granados-Carrera, “Efecto de la rehabilitación en la calidad de vida de personas con lesión medular,” *An. Fac. Med.*, vol. 81, no. 1, pp. 6–13, 2020, doi: [10.15381/anales.v81i1.16852](https://doi.org/10.15381/anales.v81i1.16852).  

4. C. P. Henao-Lema y J. E. Pérez-Parra, “Lesiones medulares y discapacidad: revisión bibliográfica,” *Aquichan*, vol. 10, no. 2, pp. 157–172, ago. 2010. [En línea]. Disponible en: [https://www.redalyc.org/articulo.oa?id=74116245006](https://www.redalyc.org/articulo.oa?id=74116245006).  

---

## Esclerosis múltiple

#### Ficha de la enfermedad
- **Nombre de la enfermedad:** Esclerosis múltiple  
- **Sistema afectado:** Afecta al sistema inmunitario, principalmente ataca a las funciones cognitivas (encéfalo) y la médula espinal. [1]  
- **Breve descripción anatómica/fisiológica:** Es una enfermedad inflamatoria desmielinizante, su nombre se debe a que daña la vaina de mielina. La La respuesta del cuerpo ante la “desmielinización” viene a ser la sensación de inestabilidad y hormigueo. De hecho, la “esclerosis múltiple” significa muchas cicatrices. [2]  

#### Factores y análisis de la enfermedad
- **Factores de riesgo principales:**  
  El principal factor de riesgo viene a ser la combinación genética (ubicado en el cromosoma 6), pues en esta enfermedad tiende a tener una susceptibilidad genética, particularmente el complejo de histocompatibilidad (HLA) [3].  
  Por otro lado, los **factores ambientales** juegan un papel importante, pues son la infección previa por el virus de **Epstein-Barr (VEB)**, niveles bajos de vitamina D y el consumo del tabaco.  

- **Manifestaciones clínicas más relevantes:**  
  Las manifestaciones son variables. Comúnmente incluye tener **distorsión visual, fatiga debilitante (80% de pacientes) y debilidad muscular [6]**. Además, es frecuente tener problemas de espasticidad, disfunciones cognitivas como la memoria, pérdida del equilibrio y coordinación.  
  Las recaídas de la EM son episodios que duran como mínimo **24 horas [7]**.  

- **Breve nota sobre el impacto funcional en la vida diaria:**  
  La esclerosis múltiple (EM) afecta la calidad de vida, volviendo dependiente al paciente de una persona externa, además afecta la movilidad.  
  Las dificultades cognitivas también afectan el empleo y las relaciones sociales, limitando a la persona a formar lazos duraderos, pues su demencia por momentos reduce la capacidad de recordar eventos pasados.  
  Además, al tener una movilidad reducida, tienen más riesgos de caídas, mientras que los problemas intestinales causan estrés social. Esto les genera una alta depresión y ansiedad significativa, haciendo el manejo de la enfermedad un desafío tanto en la forma de relacionarse como en los síntomas físicos. [8][9]  

#### Prevención, diagnóstico, tratamiento y monitoreo
- **Prevención:**  
  No existe una prevención primaria absoluta, pero es necesario un estilo de vida adecuado. Se necesita mantener niveles adecuados de vitamina D, tener una dieta equilibrada y evitar el tabaquismo [10].  
  La prevención externa también viene acompañada de **sesiones terapéuticas tempranas (TME)** para prevenir la acumulación de discapacidad a largo plazo, aprendiendo a vivir con la EM.  

- **Diagnóstico:**  
  Se basa en demostrar el desgaste/lesiones desmielinizantes en el sistema nervioso central. La **MRI** revela las lesiones características en el encéfalo y médula espinal para poder analizarlas en diferentes momentos y localizaciones [13].  

- **Tratamiento:**  
  El tratamiento es multifacético, pues incluye “inyectables, orales e infusiones” (EMRs) para reducir la actividad inflamatoria y la frecuencia de sus brotes.  
  La rehabilitación, como fisioterapia y neuropsicología, es fundamental para mantener la funcionalidad y calidad de vida.  
  El tipo de tratamiento o las medidas que se usarán se miden de acuerdo al caso de EM (recurrente-remitente, progresiva). [2,10]  

- **Monitoreo:**  
  El monitoreo es continuo para evaluar la progresión de los tratamientos. Esto requiere revisiones neurológicas regulares, escalas de discapacidad como EDSS y MRI cerebrales seriadas para detectar la actividad de la enfermedad (si existen nuevas lesiones). Además, es necesario ver la respuesta inmunitaria del paciente para ver cuáles son los efectos secundarios de los medicamentos. Por último, es necesaria una comunicación constante entre el médico y el paciente, para poder manejar la enfermedad y tener un avance real. [13]

  #### Reflexión ingenieril
- **Identificar un problema concreto:** El constante problema es en el diagnóstico, pues la evaluación hace ver los síntomas clave como la fatiga o alteración, como una de menor importancia, cuando realmente son predictores de la enfermedad. Por ello es necesario tener consultas clínicas donde se vea la fluctuación diaria del paciente, de manera óptima y personalizada. [1,2]
- **Propuesta de solución desde la ingeniería:** Desarrollar un sistema de monitoreo continuo, sin llegar a ser invasivo, pero sí amigable y fácil de entender. Con sensores inerciales (giroscopios, acelerómetros) incorporados en la pulsera, para poner la velocidad en marcha. Sería cuestión de ver la variabilidad cardiaca con el proxy, e incorporar evaluaciones, para mejoras futuras. Esta app permitirá una medicina de precisión, alertando al médico si tiene bajones, o qué tipo de terapia necesita. [1,2]

### Referencias:
1. World Health Organization, "Multiple sclerosis," Aug. 2023. [Online]. Available: [https://www.who.int/es/news-room/fact-sheets/detail/multiple-sclerosis](https://www.who.int/es/news-room/fact-sheets/detail/multiple-sclerosis). [Accessed: Aug. 27, 2025].  

2. Multiple Sclerosis International Federation, "What is MS?." [Online]. Available: [https://www.msif.org/about-ms/what-is-ms/](https://www.msif.org/about-ms/what-is-ms/). [Accessed: Aug. 27, 2025].  

3. International Multiple Sclerosis Genetics Consortium, "Multiple sclerosis genomic map implicates peripheral immune cells and microglia in susceptibility," *Science*, vol. 365, no. 6460, p. eaav7188, Sep. 2019.  

4. A. Ascherio and K. L. Munger, "Epidemiology of Multiple Sclerosis: From Risk Factors to Prevention—An Update," *Seminars in Neurology*, vol. 36, no. 02, pp. 103–114, Apr. 2016.  

5. M. P. Pender and S. R. Burrows, "Epstein-Barr virus and multiple sclerosis: potential opportunities for immunotherapy," *Clinical & Translational Immunology*, vol. 3, no. 10, p. e27, Oct. 2014.  

6. D. A. Hafler, "Multiple sclerosis," *Journal of Clinical Investigation*, vol. 113, no. 6, pp. 788–794, Mar. 2004.  

7. F. D. Lublin et al., "Defining the clinical course of multiple sclerosis: The 2013 revisions," *Neurology*, vol. 83, no. 3, pp. 278–286, Jul. 2014.  

8. A. Solari et al., "Health-related quality of life in multiple sclerosis: The impact of disability, gender and employment status," *Quality of Life Research*, vol. 15, no. 2, pp. 259–271, Mar. 2006.  

9. N. G. LaRocca, "Impact of Walking Impairment in Multiple Sclerosis," *The Patient - Patient-Centered Outcomes Research*, vol. 4, no. 3, pp. 189–201, Sep. 2011.  

10. J. Correale, M. F. Farez, and G. A. Gaitán, "Vitamin D modulation of immune responses in multiple sclerosis," *J Neurol Sci*, vol. 311, no. Suppl, p. S29, Oct. 2011.  

11. J. A. Cohen and A. T. Reder, "Therapies for multiple sclerosis: A new era of promise," *JAMA*, vol. 327, no. 12, pp. 1137–1138, Mar. 2022.  

12. A. J. Thompson et al., "Diagnosis of multiple sclerosis: 2017 revisions of the McDonald criteria," *The Lancet Neurology*, vol. 17, no. 2, pp. 162–173, Feb. 2018.  

13. M. Filippi et al., "Assessment of lesions on magnetic resonance imaging in multiple sclerosis: practical guidelines," *Brain*, vol. 142, no. 7, pp. 1858–1875, Jul. 2019.

---

## Esclerosis lateral amiotrófica 

### Ficha de la enfermedad
- **Nombre de la enfermedad:** Esclerosis lateral amiotrófica (ELA) – Amyotrophic Lateral Sclerosis (ALS) [1].  
- **Sistema afectado:** La ELA afecta al sistema nervioso central, específicamente a las motoneuronas superiores y motoneuronas inferiores. La degeneración de estas neuronas motoras lleva a debilidad, atrofia muscular y, en fases avanzadas, parálisis y compromiso respiratorio [1], [2].  
- **Breve descripción anatómica/fisiológica:** Se trata de una enfermedad neurodegenerativa progresiva y generalmente fatal, con una supervivencia media de 2 a 3 años tras el inicio de los síntomas [2]. Clínicamente, los pacientes presentan pérdida progresiva de la fuerza muscular, fasciculaciones, calambres, disartria, disfagia y deterioro respiratorio. Actualmente no existe cura; los tratamientos disponibles, como Riluzol y Edaravona, solo retrasan modestamente la progresión de la enfermedad [1][3]  

### Factores y análisis de la enfermedad: 
- **Factores de riesgo principales:** 
La ELA es una enfermedad neurodegenerativa fatal cuya causa exacta sigue sin esclarecer, pero la investigación ha identificado factores de riesgo genéticos y no genéticos que aumentan la probabilidad de desarrollarla. Dentro de los factores genéticos, destacan las mutaciones en genes como SOD1, C9orf72, TARDBP y FUS, los cuales se asocian de manera clara con la enfermedad, especialmente en los casos familiares. Además, tener antecedentes de ELA en familiares de primer grado eleva significativamente el riesgo de padecerla.[4]  
En cuanto a los factores no genéticos, se incluyen la edad avanzada y el sexo masculino, así como la exposición prolongada a metales pesados (plomo, mercurio, manganeso), pesticidas y solventes. También se han relacionado antecedentes de traumatismos craneales, la práctica de actividad física intensa o deportes competitivos, y determinadas exposiciones ocupacionales como agricultura, construcción, pintura, mecánica y campos electromagnéticos. Otros factores asociados son las quemaduras eléctricas, el servicio militar, el consumo de agua de pozo y la exposición a sustancias como formaldehído y β-N-metilamino-L-alanina (BMAA). Finalmente, se han descrito algunos factores protectores sugeridos, entre ellos un índice de masa corporal elevado y la diabetes tipo 2, los cuales parecen asociarse a un menor riesgo de desarrollar ELA según ciertos estudios.[5][6]  

- **Manifestaciones clínicas más relevantes:**
La ELA se caracteriza principalmente por la debilidad muscular progresiva debida a la degeneración de neuronas motoras, pero también presenta síntomas no motores cada vez más reconocidos. Las manifestaciones motoras principales incluyen la debilidad muscular focal y asimétrica, que suele iniciar en una extremidad o en la región bulbar (cara, lengua, faringe) y se extiende a otras áreas; la atrofia muscular, con pérdida de masa visible y palpable; las fasciculaciones, movimientos involuntarios bajo la piel; así como espasticidad e hiperreflexia, reflejo de la afectación de la motoneurona superior. De la misma manera, son frecuentes la disartria y disfagia, que dificultan el habla y la deglución, y la debilidad respiratoria, considerada la principal causa de mortalidad. Por otro lado, en las manifestaciones no motoras, pueden presentarse alteraciones cognitivas y conductuales, observándose disfunción ejecutiva, problemas de lenguaje o demencia frontotemporal en un subgrupo de pacientes. Asimismo, se describen síntomas emocionales, como episodios de risa o llanto involuntarios (afecto pseudobulbar), y otros síntomas generales como fatiga, dolor, trastornos del sueño, ansiedad y depresión. [7][8]  

- **Breve nota sobre el impacto funcional en la vida diaria :**
La Esclerosis Lateral Amiotrófica impacta de manera profunda y gradual la funcionalidad y la calidad de vida, puesto que se limita la independencia en actividades cotidianas, lo que genera una elevada carga física, emocional y social. La debilidad y atrofia muscular dificultan realizar movimientos voluntarios como caminar, levantarse, moverse y por ende, obliga al paciente al uso de una silla de ruedas o a la movilidad total; lo cual, se requieren de cuidadores y dispositivos de alimentación asistida y soporte ventilatorio.[9][10]  

### Prevención, diagnóstico, tratamiento y monitoreo
- **Prevención:**
La enfermedad de esclerosis lateral amiotrófica está precedida por síntomas prodrómicos.  
Para la prevención o el monitoreo de este padecimiento se hace uso de biomarcadores que sirven para evaluar pre síntomas y en caso de ser requerido intervenir terapéuticamente.[11]  
De acuerdo con un estudio de la Universidad de Ciencias Médicas de Cienfuegos, las personas que consumían más ácidos grasos omega 3 presentaban una reducción de riesgos del ELA en un tercio a comparación de los consumían en menor cantidad[12]  

- **Diagnóstico :**
Para determinar la esclerosis lateral amiotrófica existen los siguientes estudios : [13]  
	- **Neurofisiología:** Hace uso de electromiografía con neuroconducciones ya que con este estudio se logra identificar alteraciones sub-clínicas de la NMI.  
	- **Laboratorio:** Principalmente se recomiendan estudios de hemograma,perfil glucémico,pruebas de función renal, entre otros. Sirven para 		           		descartar trastornos que pueden simular síndromes de neuronas motoras.  
	- **Neuroimágenes:** El rol de este estudio es descartar otras causas de un síndrome piramidal como tumores del neuroeje,mielopatías, enfermedades 				cerebrovasculares,etc.  

- **Tratamiento:**
El tratamiento de la ELA está centrado en ralentizar su progresión, manejar los síntomas y con ello tener una buena calidad de vida. El pilar farmacológico tiene de principal al Riluzol que prolonga la supervivencia y modula el glutamato, y Edaravona que es un antioxidante que reduce el estrés oxidativo y reduce el deterioro del paciente. Además, es necesario el manejo sistemático que incluye el soporte respiratorio, soporte nutricional, terapia física, medicamentos para tratar el dolor, espasticidad, la sialorrea, entre otros. El tratamiento engloba un tratamiento con una serie de fases que ayudan a la persona a tener una mejor calidad de vida y tener un avance de mejoría con respecto a la enfermedad. [14]  

- **Monitoreo:**
El monitoreo en la ELA es un proceso continuo y sistemático para evaluar la progresión de la enfermedad, ajustar tratamientos y anticipar complicaciones. Por ello, su objetivo es mantener la mejor calidad de vida posible y adaptar el manejo clínico a las necesidades cambiantes del paciente. Este monitoreo se realiza mediante escalas funcionales, la más utilizada es ALSFRS-R (Escala Funcional Revisada para ELA) que se encarga de medir la capacidad para ejecutar actividades diarias y se aplica periódicamente para detectar cambios en la funcionalidad del paciente; evaluaciones respiratorias para detectar precozmente insuficiencia; valoración nutricional, y el uso de tecnología portátil y biomarcadores que están revolucionando la precisión y la frecuencia del seguimiento. [15][16]

### Reflexión ingenieril:
Se plantea un desafío complejo en el ámbito neurológico, ya que progresa con la pérdida gradual de motoneuronas, lo que conlleva a debilidad muscular, parálisis y fallas en funciones vitales como la respiración y la deglución. Desde la ingeniería biomédica, esta condición demanda soluciones que vayan más allá de los tratamientos farmacológicos limitados disponibles hoy en día. Se puede potenciar la calidad de vida de los pacientes mediante tecnologías de asistencia, como interfaces cerebro-computadora que permitan comunicarse incluso en etapas avanzadas, sistemas de ventilación no invasivos que se adapten a la función respiratoria del paciente, dispositivos de seguimiento que monitorizan la progresión de la enfermedad en tiempo real y, en un futuro, terapias de estimulación neuronal o bioimpresión de tejidos que busquen ralentizar la degeneración. 

### Referencias:
1. Centers for Disease Control and Prevention (CDC), “About Amyotrophic Lateral Sclerosis (ALS),” *Public Health Web Page*, Nov. 2024. [En línea]. Disponible en: [https://www.cdc.gov/als/abouttheregistrymain/about-amyotrophic-lateral-sclerosis-als.html](https://www.cdc.gov/als/abouttheregistrymain/about-amyotrophic-lateral-sclerosis-als.html).  

2. World Health Organization (WHO) / IARC, *Neurodegenerative Diseases*. Lyon: IARC Press, 2004. [En línea]. Disponible en: [https://publications.iarc.who.int/_publications/media/download/1417/216854435872ac5290e8f42b446ab20a9e5531f8.pdf](https://publications.iarc.who.int/_publications/media/download/1417/216854435872ac5290e8f42b446ab20a9e5531f8.pdf).  

3. Centers for Disease Control and Prevention (CDC), “National ALS Registry: Impact, Challenges, and Future Directions,” *MMWR Morbidity and Mortality Weekly Report*, vol. 66, Dec. 2017. [En línea]. Disponible en: [https://www.cdc.gov/mmwr/volumes/66/wr/mm6650a3.htm](https://www.cdc.gov/mmwr/volumes/66/wr/mm6650a3.htm).  

4. C. Ingre, P. Roos, F. Piehl, F. Kamel, & F. Fang, “Risk factors for amyotrophic lateral sclerosis,” *Clinical Epidemiology*, vol. 7, pp. 181–193, 2015. doi: [10.2147/CLEP.S37505](https://doi.org/10.2147/CLEP.S37505).  

5. Q. Duan et al., “Risk factors of amyotrophic lateral sclerosis: a global meta-summary,” *Frontiers in Neuroscience*, vol. 17, 2023. doi: [10.3389/fnins.2023.1177431](https://doi.org/10.3389/fnins.2023.1177431).  

6. A. Andrew et al., “Risk factors for amyotrophic lateral sclerosis: A regional United States case‐control study,” *Muscle & Nerve*, vol. 63, pp. 52–59, 2020. doi: [10.1002/mus.27085](https://doi.org/10.1002/mus.27085).  

7. M. Vidovic et al., “Current State and Future Directions in the Diagnosis of Amyotrophic Lateral Sclerosis,” *Cells*, vol. 12, 2023. doi: [10.3390/cells12050736](https://doi.org/10.3390/cells12050736).  

8. D. Yuan, S. Jiang, & R. Xu, “Clinical features and progress in diagnosis and treatment of amyotrophic lateral sclerosis,” *Annals of Medicine*, vol. 56, 2024. doi: [10.1080/07853890.2024.2399962](https://doi.org/10.1080/07853890.2024.2399962).  

9. S. Siqueira et al., “Quality of life of patients with Amyotrophic Lateral Sclerosis,” *Northeast Network Nursing Journal*, vol. 18, pp. 139–146, 2017. doi: [10.15253/2175-6783.2017000100019](https://doi.org/10.15253/2175-6783.2017000100019).  

10. C. Caballero-Eraso et al., “Prospective study to evaluate quality of life in amyotrophic lateral sclerosis,” *Scientific Reports*, vol. 13, 2023. doi: [10.1038/s41598-023-39147-w](https://doi.org/10.1038/s41598-023-39147-w).  

11. FUNDELA, “Prevención de la esclerosis lateral amiotrófica: conocimientos de las enfermedades neurodegenerativas presintomáticas,” 2022. [Online]. Disponible en: [https://www.fundela.es/noticias/investigacion/prevencion-de-la-esclerosis-lateral-amiotrofica-conocimientos-de-las-enfermedades-neurodeg/](https://www.fundela.es/noticias/investigacion/prevencion-de-la-esclerosis-lateral-amiotrofica-conocimientos-de-las-enfermedades-neurodeg/).  

12. *Rev Finlay*, “Nutrición: Una dieta rica en ácidos grasos omega 3 podría prevenir la esclerosis lateral amiotrófica.” [Online]. Disponible en: [https://revfinlay.sld.cu/index.php/finlay/announcement/view/694](https://revfinlay.sld.cu/index.php/finlay/announcement/view/694).  

13. C. H. Zapata-Zapata, E. Franco-Dáger, J. M. Solano-Atehortúa, y L. F. Ahunca-Velásquez, “Esclerosis lateral amiotrófica: actualización,” *Iatreia*, vol. 29, no. 2, pp. 194–205, abr.–jun. 2016. doi: [10.17533/udea.iatreia.v29n2a08](https://doi.org/10.17533/udea.iatreia.v29n2a08).  

14. M. A. G. Vucic, “Riluzole: a review of its pharmacologic properties and clinical efficacy in amyotrophic lateral sclerosis,” *Neuropsychiatric Disease and Treatment*, vol. 16, pp. 1171–1185, 2020.  

15. N. Simon et al., “Quantifying Disease Progression in Amyotrophic Lateral Sclerosis,” *Annals of Neurology*, vol. 76, pp. 643–657, 2014. doi: [10.1002/ana.24273](https://doi.org/10.1002/ana.24273).  

16. M. Dreger et al., “Cerebrospinal fluid biomarkers of disease activity and progression in amyotrophic lateral sclerosis,” *Journal of Neurology, Neurosurgery, and Psychiatry*, vol. 93, pp. 422–435, 2022. doi: [10.1136/jnnp-2021-327503](https://doi.org/10.1136/jnnp-2021-327503).

## Amputaciones

## Ficha de la enfermedad

Las amputaciones no son una enfermedad en sí, sino una consecuencia de diversas patologías que afectan principalmente al sistema **musculoesquelético** y **vascular**. 

Son procedimientos médicos en los que se remueve una extremidad de forma **parcial**, para rescatar la mayor parte y preservar la función, o **totalmente**, cuando la extremidad está completamente dañada y el riesgo para la vida del paciente es inminente. 

Entre las principales condiciones asociadas destacan:  
- **Diabetes mellitus**: responsable de la mayoría de amputaciones no traumáticas en miembros inferiores.  
- **Enfermedad arterial periférica (EAP)**: al producir obstrucción arterial constituye la causa más frecuente de amputaciones mayores y de mortalidad hospitalaria tras la cirugía.  
- **Trauma y neuropatía**, en menor medida.  

El sistema afectado involucra tanto al **musculoesquelético** (huesos, músculos, tendones y articulaciones) como al **vascular** (arterias y venas de las extremidades, en especial cuando existe isquemia por EAP o microangiopatía diabética).  

Desde el punto de vista anatómico, las amputaciones pueden clasificarse en:  
- **Menores**: dedos, pie.  
- **Mayores**: por encima del tobillo o rodilla.  

Desde el punto de vista fisiológico, se relacionan con la **pérdida de irrigación sanguínea, necrosis tisular y daño irreversible**, lo que hace necesaria la remoción para prevenir infecciones y complicaciones sistémicas.  

El **nivel de amputación** depende de la viabilidad de los tejidos blandos y de la capacidad de cubrir adecuadamente el hueso remanente. [1][2]  

---

## Factores y análisis de la enfermedad

Los **factores de riesgo** que más destacan son los siguientes:  
- Mayor incidencia en hombres.  
- Tabaquismo.  
- Úlceras previas.  
- Gangrena.  
- Mal control glucémico (HbA1c elevada).  
- Índice tobillo-brazo bajo (indicador de enfermedad arterial periférica).  
- Comorbilidades cardiovasculares.  
- Edad avanzada.  
- Insuficiencia renal.  
- Marcadores inflamatorios elevados como leucocitosis, proteína C reactiva, NRL (índice neutrófilo-linfocito) y anemia. [3][4]  

Adicionalmente, las **manifestaciones clínicas más relevantes** por las amputaciones incluyen:  
- Úlceras crónicas que no cicatrizan.  
- Infecciones recurrentes.  
- Gangrena.  
- Dolor persistente.  
- **Dolor neuropático**, que afecta hasta un 21% de los pacientes y reduce la calidad de vida.  
- Signos de isquemia: piel fría, palidez y ausencia de pulsos distales. [5]  

El **impacto funcional** llega a ser muy significativo en la vida diaria, ya que muchos pacientes requieren muletas, silla de ruedas o prótesis. Solo un porcentaje logra caminar de forma independiente tras amputaciones mayores.  

Asimismo, las amputaciones afectan de manera **psicológica y social**, provocando depresión, ansiedad y dificultades para reintegrarse al trabajo y la comunidad. [6]  

---

## Prevención, diagnóstico, tratamiento y monitoreo

**Prevención**  
- Control de factores de riesgo (p. ej., control estricto de la glucosa en diabéticos).  
- Educación y cuidado del paciente.  
- Políticas de salud pública.  
- Equipos multidisciplinarios integrados por diabetólogos, cirujanos, podólogos, enfermeros y rehabilitadores.  

**Diagnóstico**  
- Inspección clínica.  
- Pruebas vasculares.  
- Clasificación de lesiones mediante el uso de escalas de riesgo.  

**Tratamiento**  
- Manejo de infecciones y heridas.  
- Revascularización.  
- Cirugía conservadora.  
- Manejo del dolor.  

**Monitoreo**  
- Seguimiento estructurado.  
- Rehabilitación y soporte psicológico.  
- Educación continua.  

---

## Reflexión ingenieril

Basándonos en lo expuesto anteriormente, se identifica que la mayor necesidad de las personas amputadas es **recuperar la autonomía y funcionalidad** en la vida diaria. [7]  

Por tal motivo, las **tecnologías biomédicas actuales** pueden abordar problemas críticos en la atención de personas con riesgo de amputación o con discapacidad, especialmente en las áreas de:  
- Monitorización continua.  
- Mejora de la movilidad.  
- Facilitación de la comunicación.  

En resumen, el reto principal es **mejorar la precisión, comodidad y personalización** de los dispositivos existentes, así como su integración adecuada en la cotidianidad.  

De este modo, se busca desarrollar soluciones innovadoras para una atención más efectiva y centrada en el paciente y su calidad de vida.

### Referencias

1. Narres, M., Kvitkina, T., Claessen, H., Droste, S., Schuster, B., Morbach, S., Rümenapf, G., Van Acker, K., & Icks, A. (2017). Incidence of lower extremity amputations in the diabetic compared with the non-diabetic population: A systematic review. *PLoS ONE*, 12. https://doi.org/10.1371/journal.pone.0182081.  
2. Portela, F., Louzada, A., Da Silva, M., Teivelis, M., Kuzniec, S., & Wolosker, N. (2024). Analysis of Lower Limb Amputations in Brazil's Public Health System over 13 Years. *European Journal of Vascular and Endovascular Surgery: the official journal of the European Society for Vascular Surgery.* https://doi.org/10.1016/j.ejvs.2024.02.028.  
3. Hallström, S., Svensson, A., Pivodic, A., Ólafsdóttir, A., Löndahl, M., Wedel, H., & Lind, M. (2021). Risk factors and incidence over time for lower extremity amputations in people with type 1 diabetes: an observational cohort study of 46,088 patients from the Swedish National Diabetes Registry. *Diabetologia*, 64, 2751 - 2761. https://doi.org/10.1007/s00125-021-05550-z.  
4. Zhang, X., Li, Q., Zhou, X., Xu, Y., Shu, Z., & Deng, H. (2024). Risk factors for amputation in diabetic foot ulcers: A retrospective analysis. *International Wound Journal*, 21. https://doi.org/10.1111/iwj.14832.  
5. Gong, H., Ren, Y., Li, Z., Zha, P., Bista, R., Li, Y., Chen, D., Gao, Y., Chen, L., Ran, X., & Wang, C. (2023). Clinical characteristics and risk factors of lower extremity amputation in the diabetic inpatients with foot ulcers. *Frontiers in Endocrinology*, 14. https://doi.org/10.3389/fendo.2023.1144806.  
6. Rathnayake, A., Saboo, A., Malabu, U., & Falhammar, H. (2020). Lower extremity amputations and long-term outcomes in diabetic foot ulcers: A systematic review. *World Journal of Diabetes*, 11, 391 - 399. https://doi.org/10.4239/wjd.v11.i9.391.  
7. Rodrigues, D., Carvalho, L., & Pinto, C. (2025). Lower-Limb Amputees and Family Caregivers: Challenges, Needs, and Strategies for Empowerment—A Qualitative Study. *Nursing Reports*, 15. https://doi.org/10.3390/nursrep15050166.

## Escoliosis

### Ficha de la enfermedad
○ Nombre de la enfermedad: Escoliosis - Definida como una una curvatura lateral en la columna vertebral de al menos 10 grados según la escala de Cobbs. [1]  
○Sistema afectado: El sistema principalmente afectado es el musculoesquelético, debido a que las deformaciones afectan a la columna vertebral y las rotaciones de las vértebras. [2]  
○ Breve descripción anatómica/fisiológica  
La escoliosis se define como una deformidad tridimensional de la columna vertebral, caracterizada principalmente por una curvatura lateral mayor de 10 grados en el plano coronal, acompañada de rotación vertebral y, frecuentemente, alteraciones en los planos sagital y axial. Es un síntoma, no una enfermedad en sí misma, y puede afectar a cualquier segmento de la columna( cervical, dorsal, lumbar)[1], [2].
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

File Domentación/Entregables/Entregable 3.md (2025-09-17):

<div align="center">

# Fundamentos de Biodiseño: Entregable Nº 3 

</div>
<div align="center">
  
## Contenido:
</div>

### Caso de referencia:
#### Caso 1: Escoliosis congénita (niño pequeño):

<div align="justify">
  
Edad: Niño de 1 año con 10 meses
Diagnóstico: Escoliosis congénita asociada a hemivértebra y agenesia de costilla, tratado con un dispositivo quirúrgico especial (VEPTR, un implante expansible)
Situación general: El paciente requería de controles constantes debido al avance de la curvatura anormal de la columna vertebral. Su anatomía en particular dificultaba el uso de técnicas estándar, lo que forzó a un tratamiento más individualizado.
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

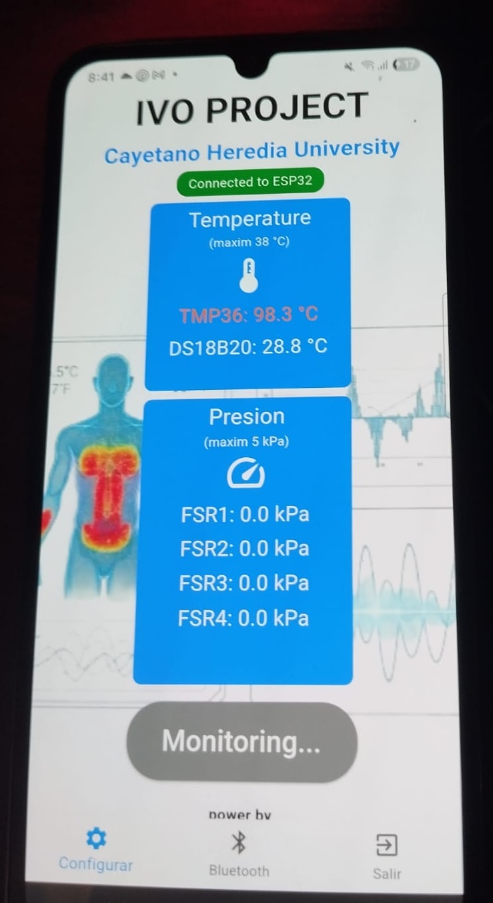
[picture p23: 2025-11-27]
Domentación/Entregables/Hito 2/App-2.jpg

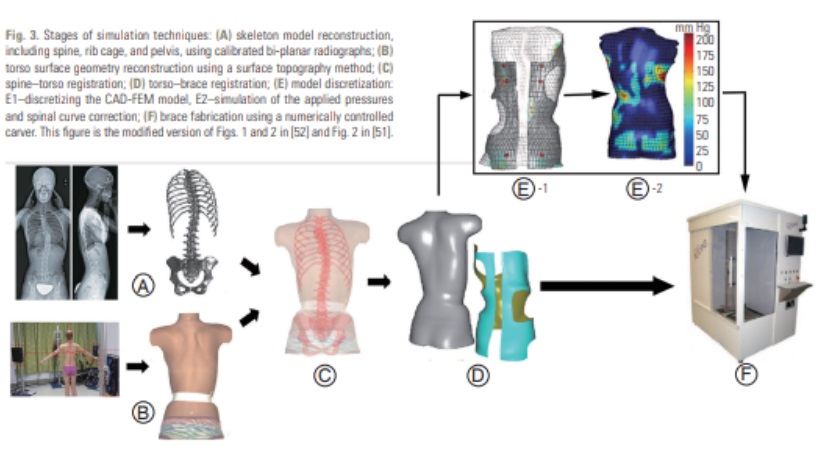
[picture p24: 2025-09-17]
Imagenes/Recursos entregrable 4/serial.jpg

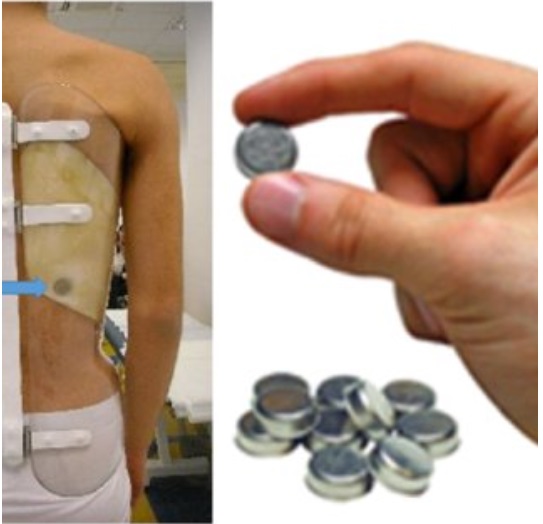
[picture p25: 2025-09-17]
Imagenes/Recursos entregrable 4/thermobrace.jpg

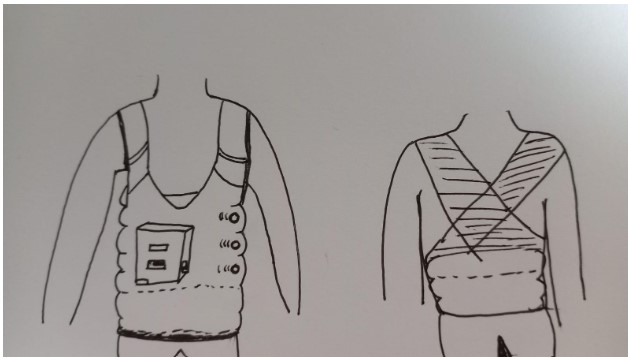
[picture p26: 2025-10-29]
Imagenes/Recursos entregable 9/Captura de pantalla 2025-10-29 004342.jpg

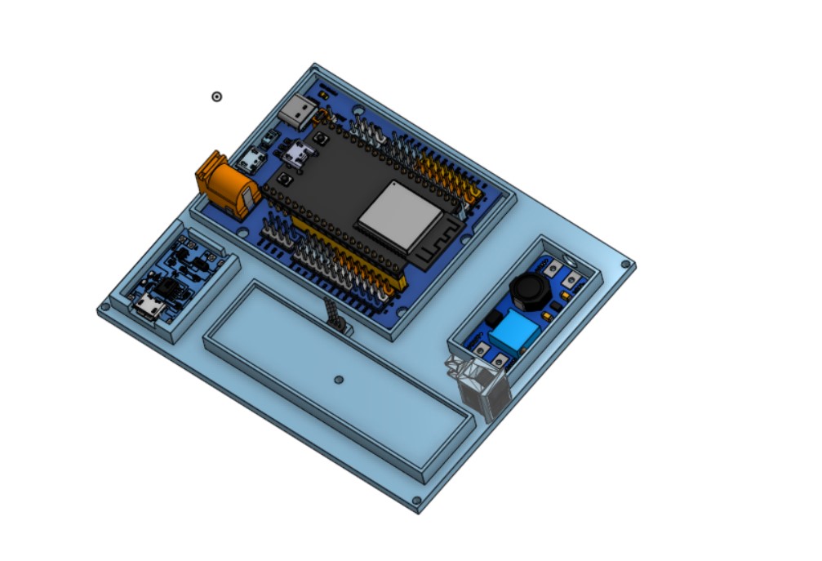
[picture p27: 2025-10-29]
Imagenes/Recursos entregable 9/Captura de pantalla 2025-10-29 000337.jpg

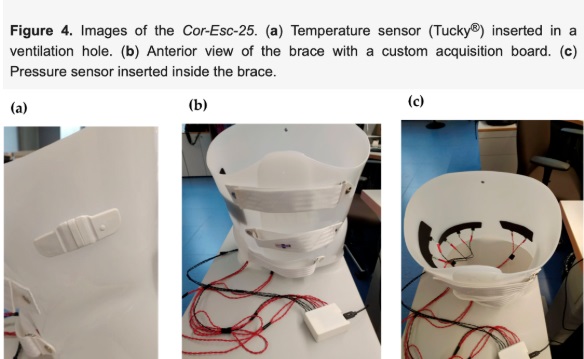
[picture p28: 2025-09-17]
Imagenes/Recursos entregrable 4/corerc.jpg

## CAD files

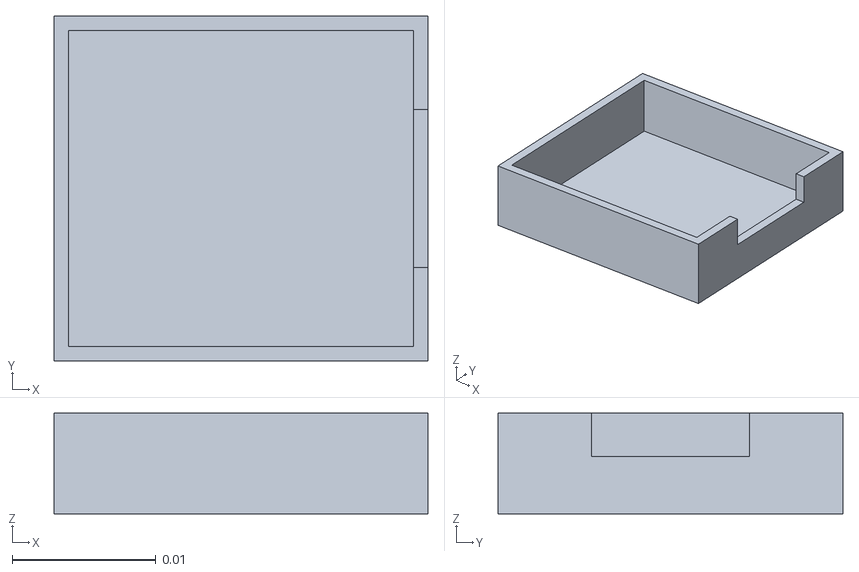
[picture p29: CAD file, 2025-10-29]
Domentación/Entregables/Entregable 9/Modelado 3d/STL/Montura para modulo de sensor de vibracion.stl
0.026 x 0.024 x 0.007

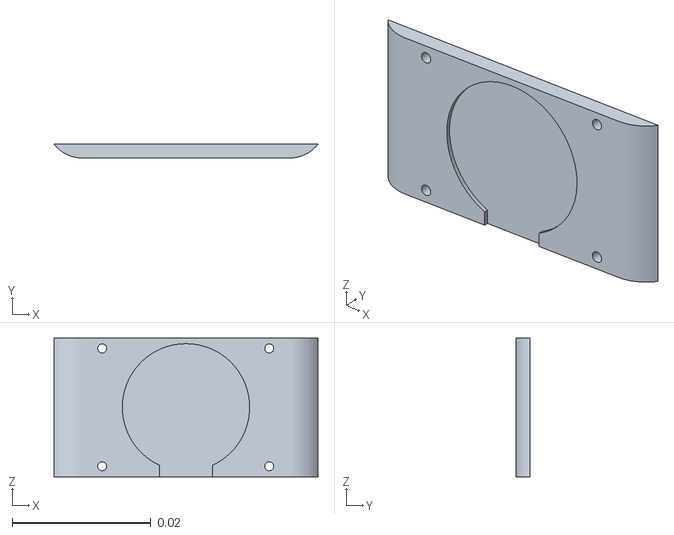
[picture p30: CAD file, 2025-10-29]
Domentación/Entregables/Entregable 9/Modelado 3d/STL/Sensor de fuerza FSR-402 MONTURA.stl
0.038 x 0.002 x 0.02

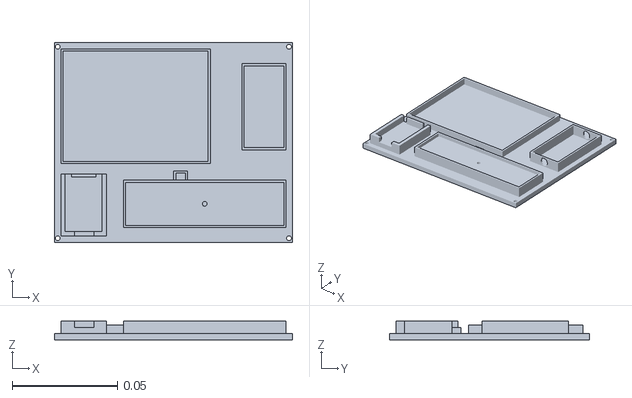
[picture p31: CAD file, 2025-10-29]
Domentación/Entregables/Entregable 9/Modelado 3d/STL/Case principal Base.stl
0.113 x 0.095 x 0.009

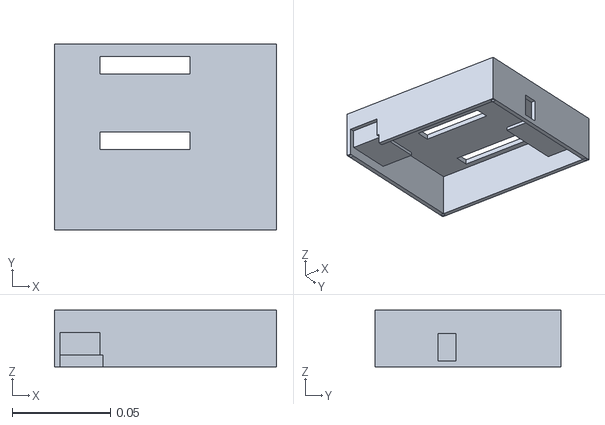
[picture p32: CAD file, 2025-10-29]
Domentación/Entregables/Entregable 9/Modelado 3d/STL/Case principal Techo.stl
0.113 x 0.095 x 0.029

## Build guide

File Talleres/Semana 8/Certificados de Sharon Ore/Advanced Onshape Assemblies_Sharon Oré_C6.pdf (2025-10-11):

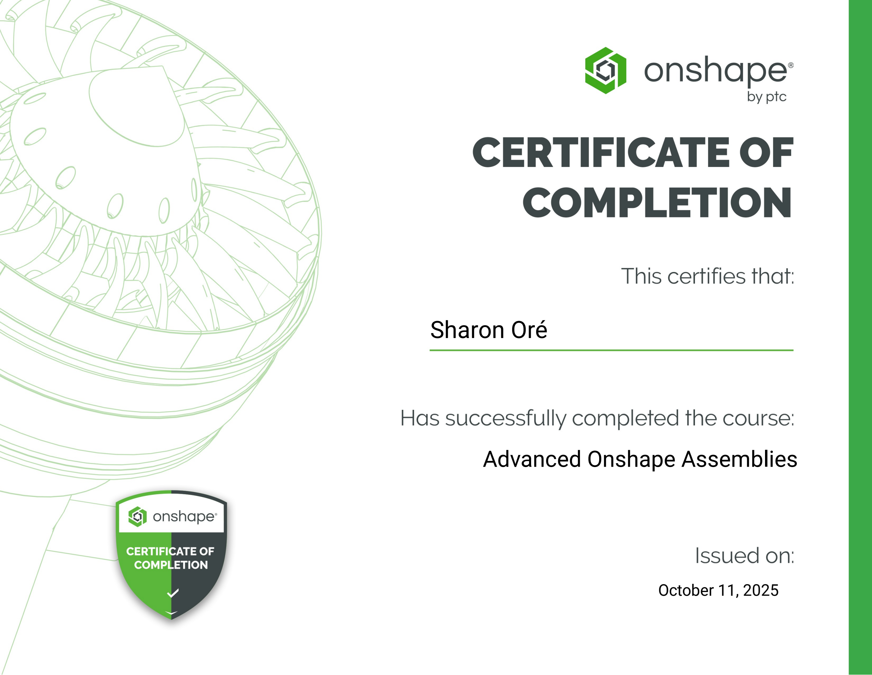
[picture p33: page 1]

Sharon Oré

Advanced Onshape Assemblies

October 11, 2025

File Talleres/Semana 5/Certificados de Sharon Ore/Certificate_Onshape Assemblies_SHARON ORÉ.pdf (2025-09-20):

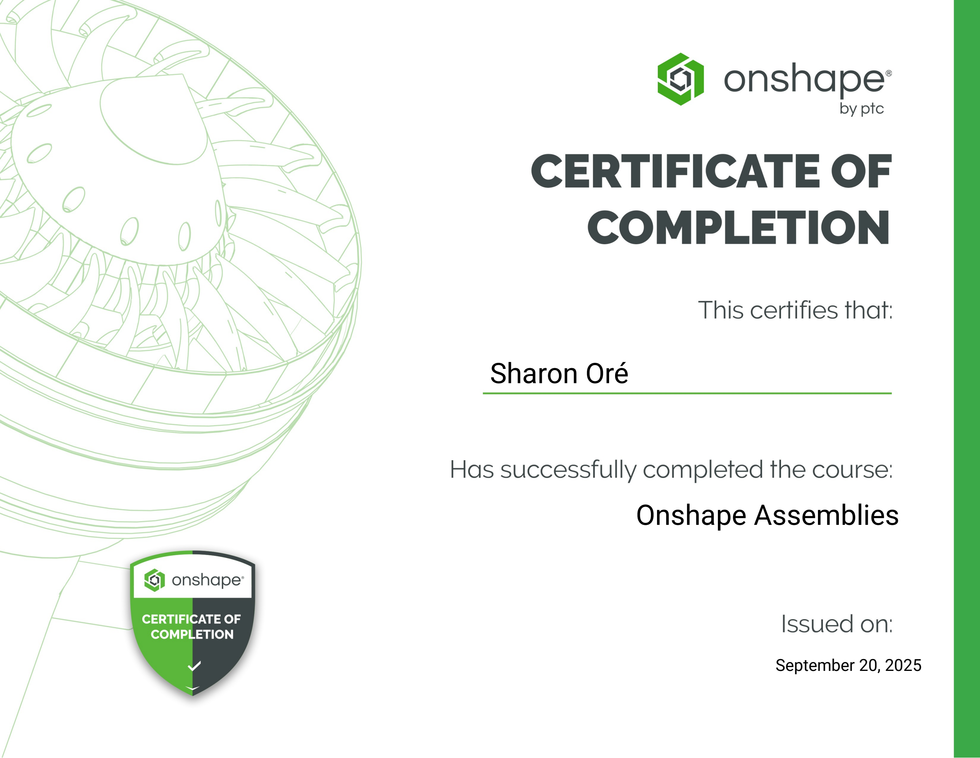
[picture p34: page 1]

Sharon Oré

September 20, 2025

Onshape Assemblies

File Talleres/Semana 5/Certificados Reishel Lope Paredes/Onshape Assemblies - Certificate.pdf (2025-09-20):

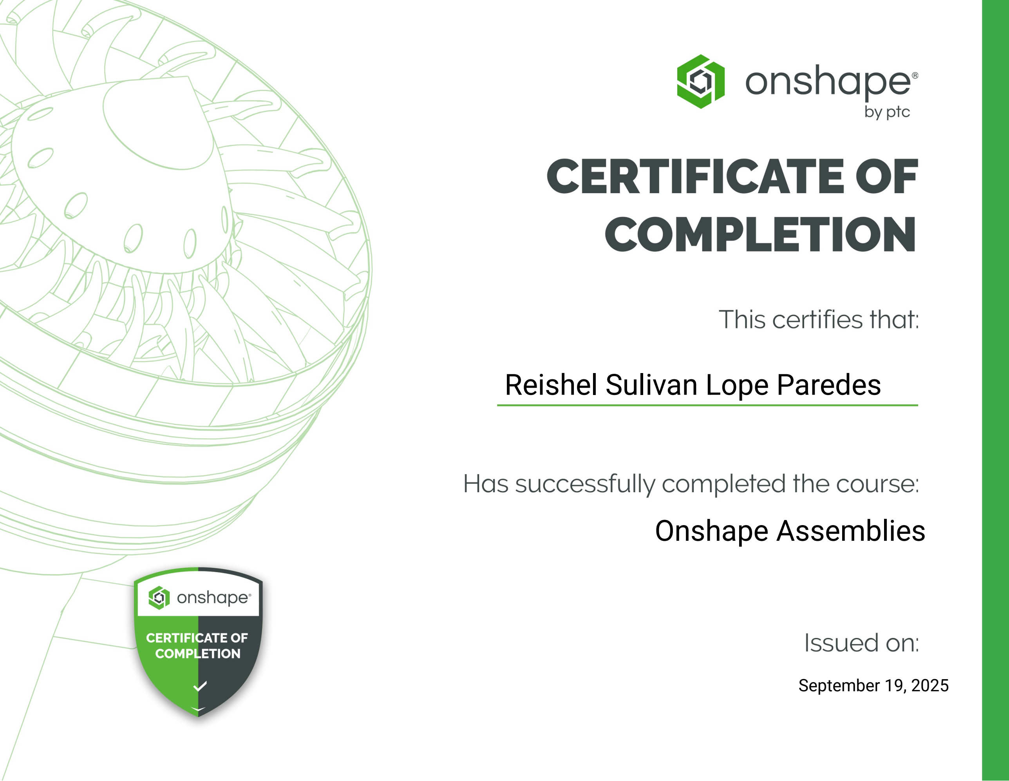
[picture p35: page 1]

Reishel Sulivan Lope Paredes

September 19, 2025

Onshape Assemblies

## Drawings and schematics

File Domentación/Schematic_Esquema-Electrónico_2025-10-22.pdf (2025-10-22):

# M dulo de carga y protecci n TP4056 (USB-C)

# Sensor de temperatura

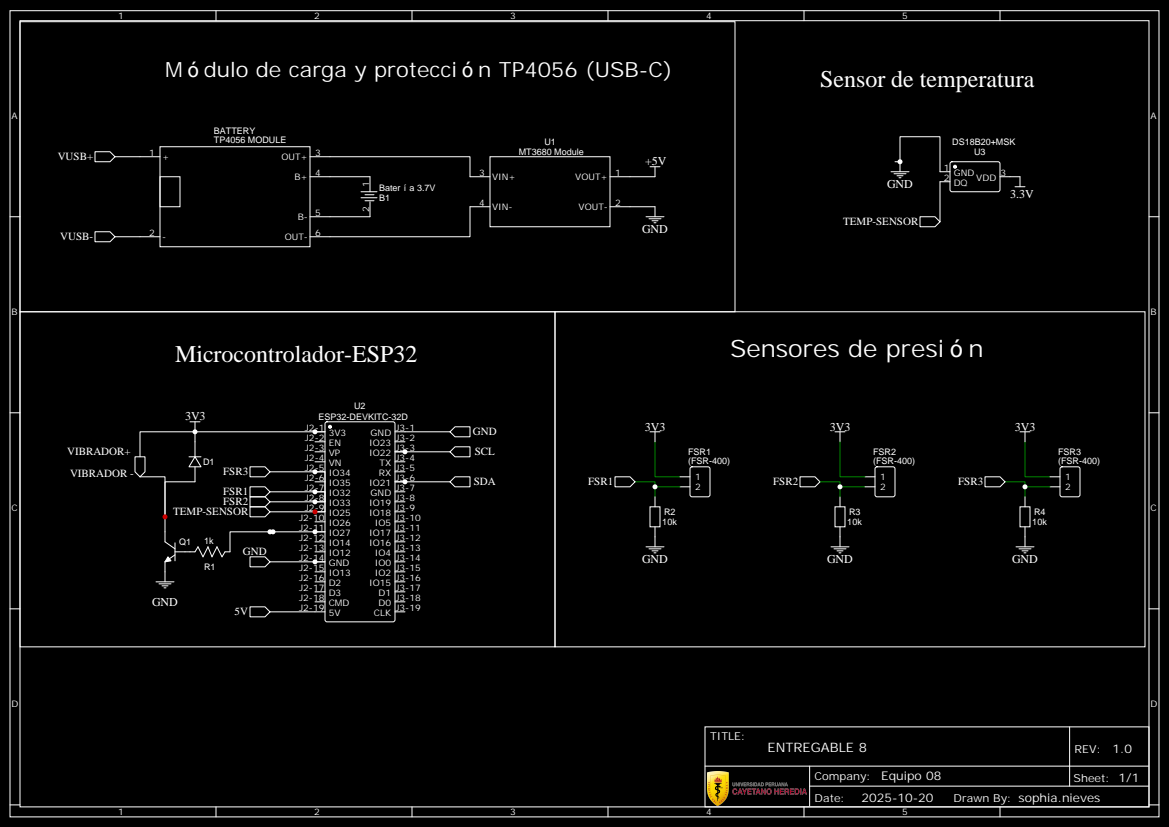
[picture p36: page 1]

Drawn By: sophia.nieves

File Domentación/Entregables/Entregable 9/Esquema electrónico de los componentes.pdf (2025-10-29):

# M dulo de carga y protecci n TP4056 (USB-C)

# Motor de vibraci n

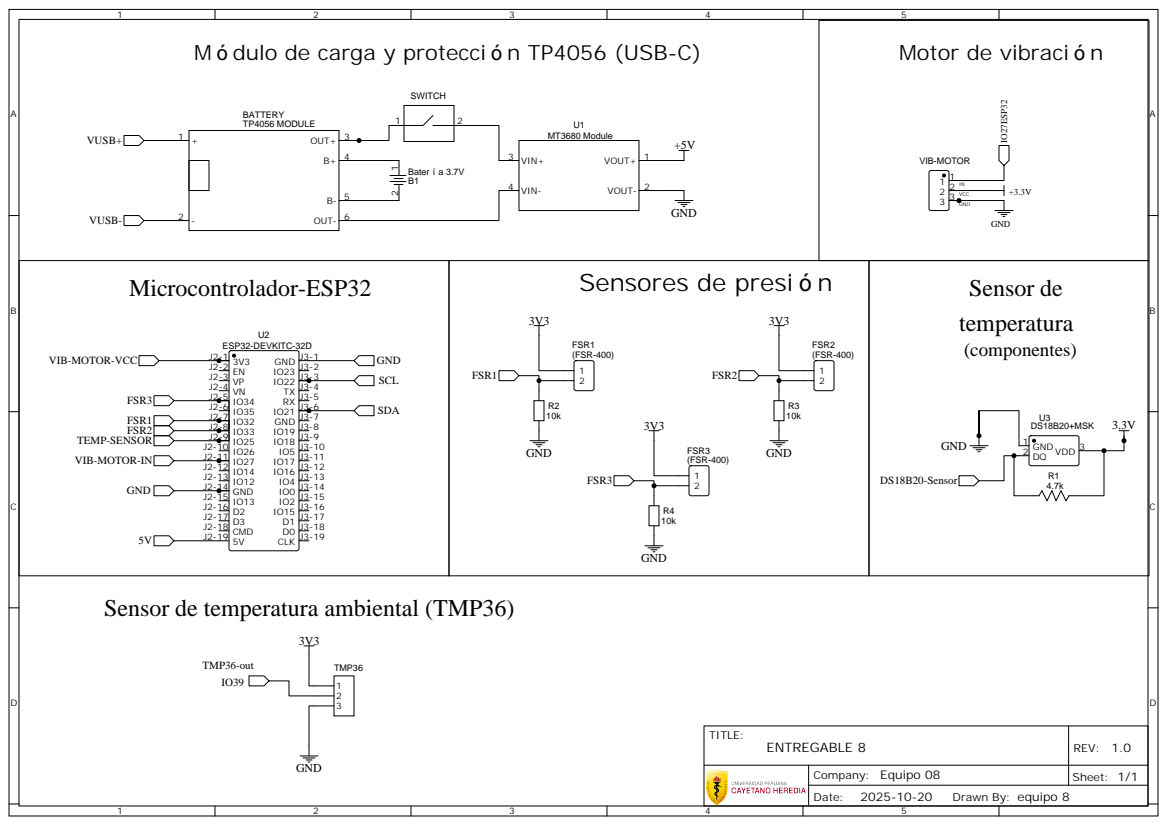
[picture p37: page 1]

Sensor de temperatura ambiental (TMP36)

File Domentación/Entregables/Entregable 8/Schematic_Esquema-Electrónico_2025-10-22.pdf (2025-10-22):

# M dulo de carga y protecci n TP4056 (USB-C)

# Motor de vibraci n

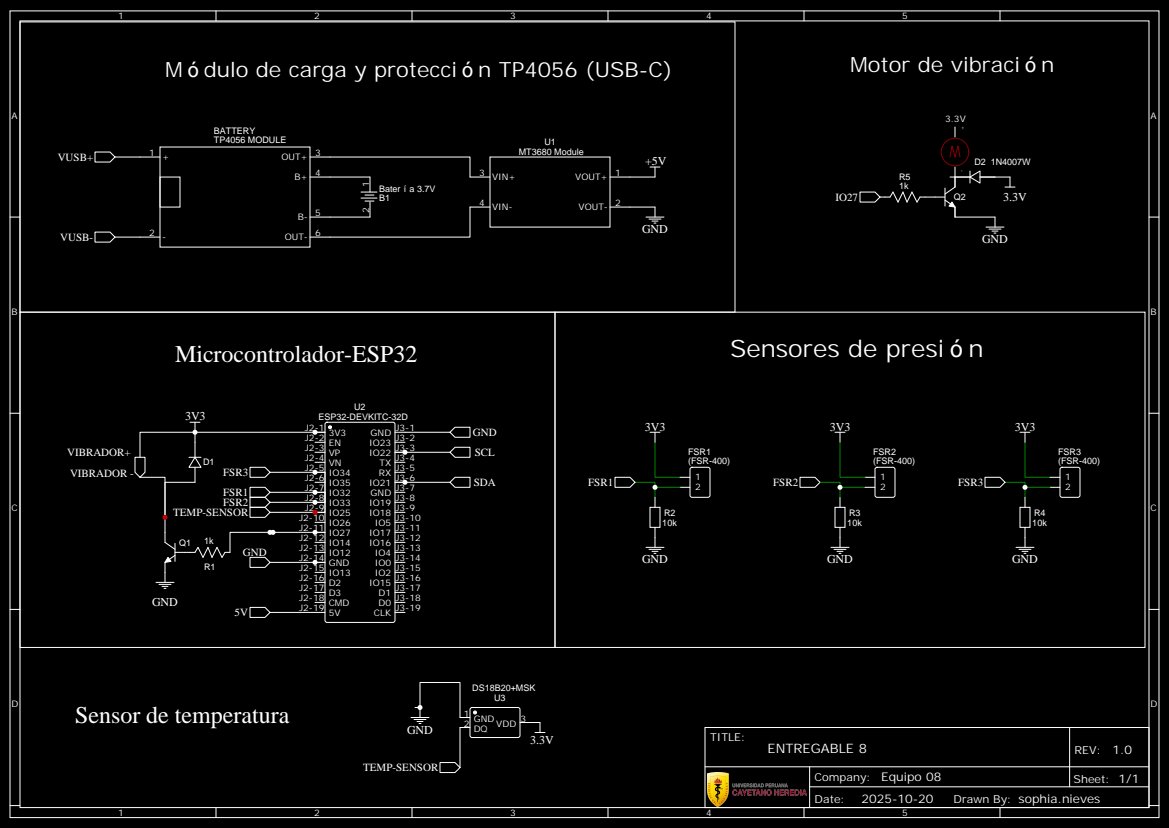
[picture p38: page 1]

Drawn By: sophia.nieves

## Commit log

2025-08-23 reorganizacion de carpetas
2025-09-20 Certificados de Daniela Ochoa
2025-10-11 Reorganización de carpetas talleres
2025-10-22 img fsr case
2025-10-29 planos y stl
    [Case principal Base.stl, Case principal Techo.stl, Sensor de fuerza FSR-402 MONTURA.stl]
2025-10-29 modelado 3d
    [Montura para modulo de sensor de vibracion.stl]
